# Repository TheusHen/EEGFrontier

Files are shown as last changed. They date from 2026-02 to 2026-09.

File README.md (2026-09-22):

# EEGFrontier V1



> [!WARNING]
> **Hardware V2 Under Development**
> The current version of this project (V1) has pending schematic and layout revisions. **V2 is under active development** with all necessary fixes. If you plan to fabricate or assemble this board, please **wait for the official V2 tag and release** before sending files to the fab.

EEGFrontier V1 is a compact EEG acquisition board built around the **ADS1299-4PAGR** and a **Seeed XIAO RP2040**.

This repository contains:
- Hardware design files (KiCad)
- Firmware (PlatformIO / Arduino)
- Project assets and documentation images

## Important Notice

Please check the `bom/` folder for the Bill of Materials and pricing information. A dedicated folder was created specifically to document BOM details and cost references.

## Short Project Description

**EEGFrontier V1** is an open-source EEG acquisition board designed to capture real brain signals and stream them in real time to a computer for analysis and visualization.
It focuses on learning, experimentation, and understanding attention and focus using raw EEG data.

---

## How to Use the Project

The board connects to EEG electrodes and streams data over USB to a computer.
Users flash the firmware to the XIAO RP2040, connect electrodes to the header, and read real-time EEG data using serial tools or custom software written in any language.

## Why I Made This Project

I made EEGFrontier to learn how real EEG hardware works beyond black-box consumer devices.
The goal is to make neurotechnology more accessible to students by providing a platform where raw signals, hardware design, and firmware are fully open and modifiable.

---

## Project Concept

The board is designed to connect dry electrodes and stream real-time data from the EEG channels.

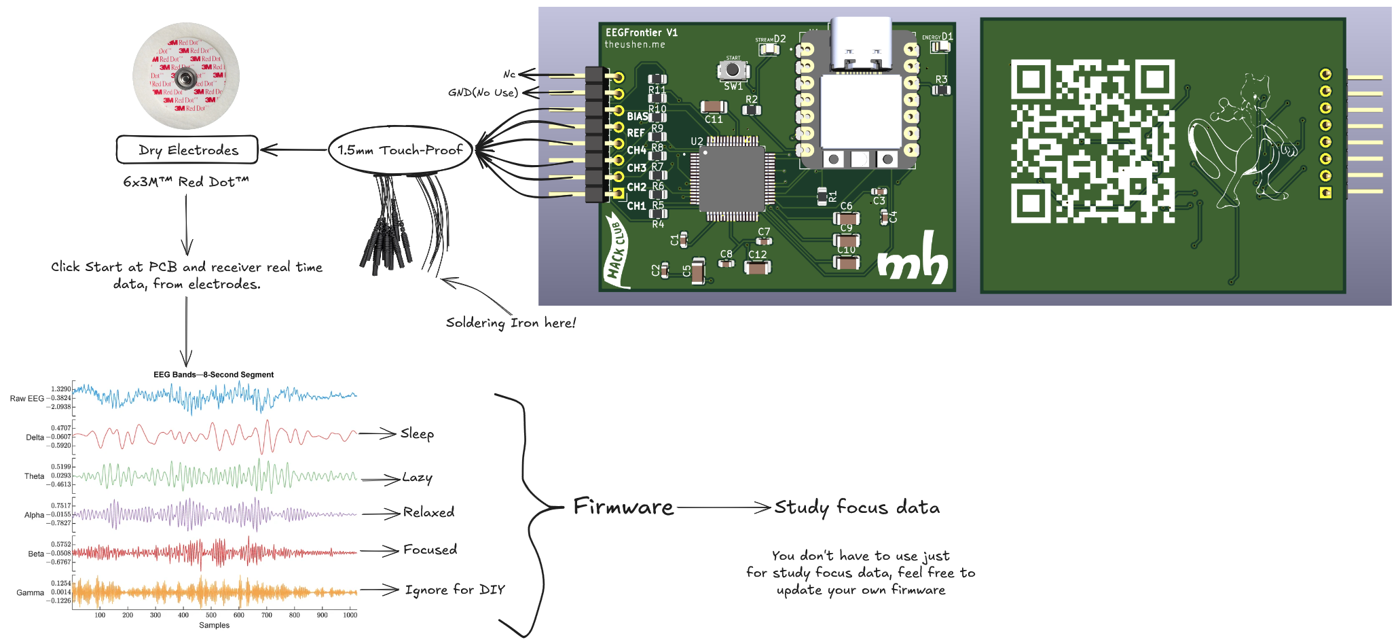
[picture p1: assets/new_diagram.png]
EEGFrontier concept and wiring overview V2


## Hardware Overview

### 3D View (Front)

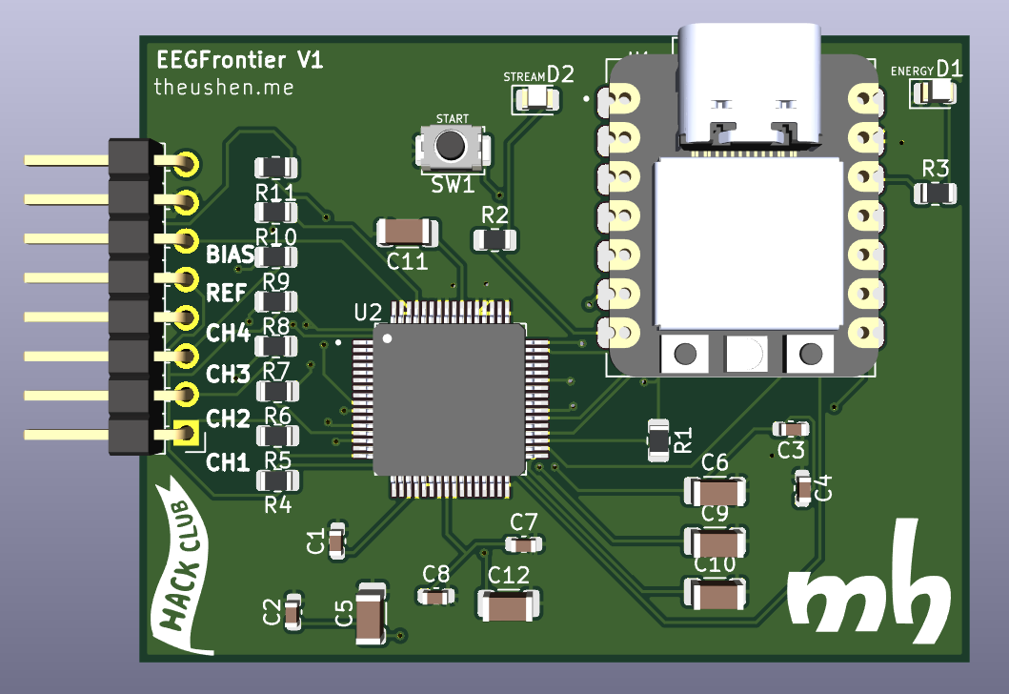
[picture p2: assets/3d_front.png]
EEGFrontier V1 3D front view


### 3D View (Back)

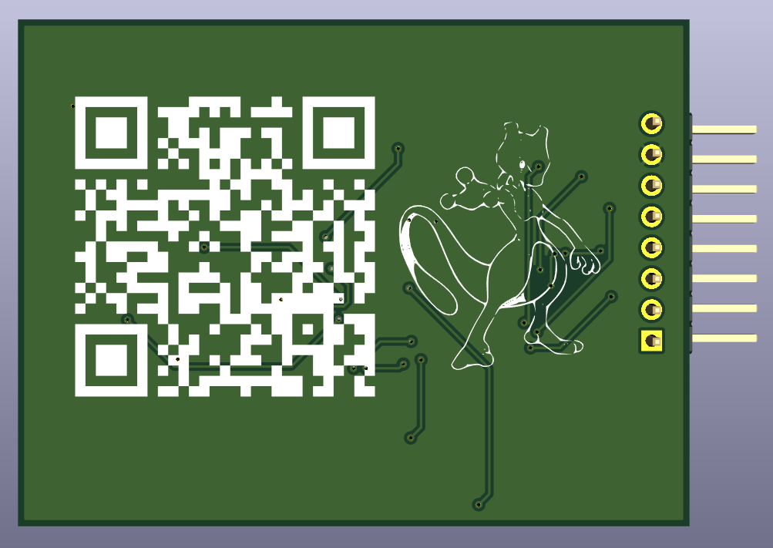
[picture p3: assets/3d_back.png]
EEGFrontier V1 3D back view


### PCB Layout

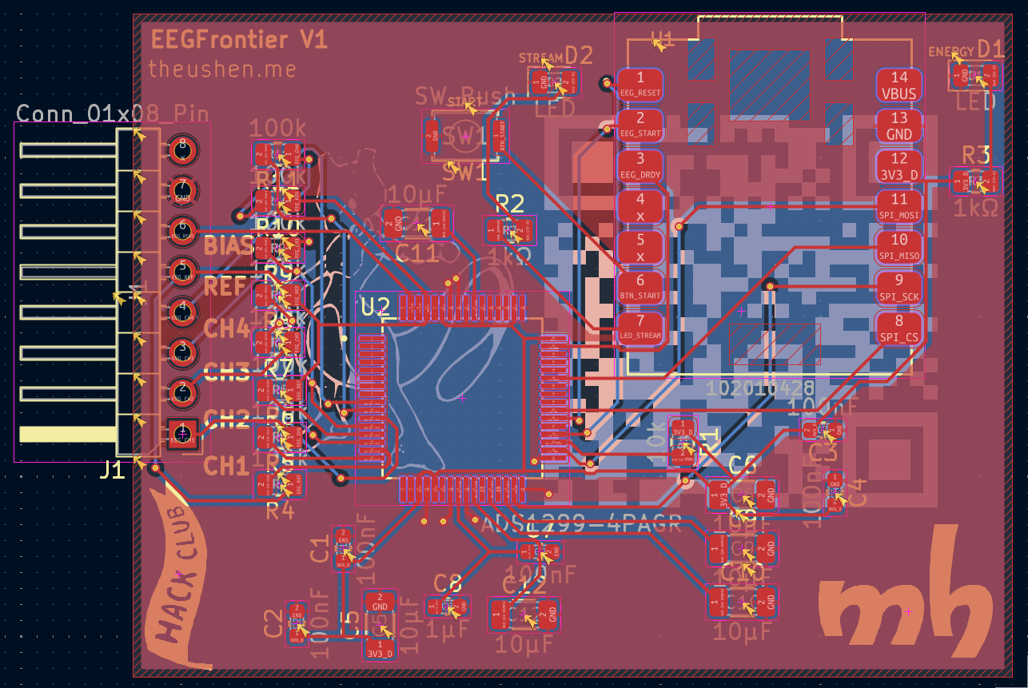
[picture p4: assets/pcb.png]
EEGFrontier V1 PCB layout


### Schematic

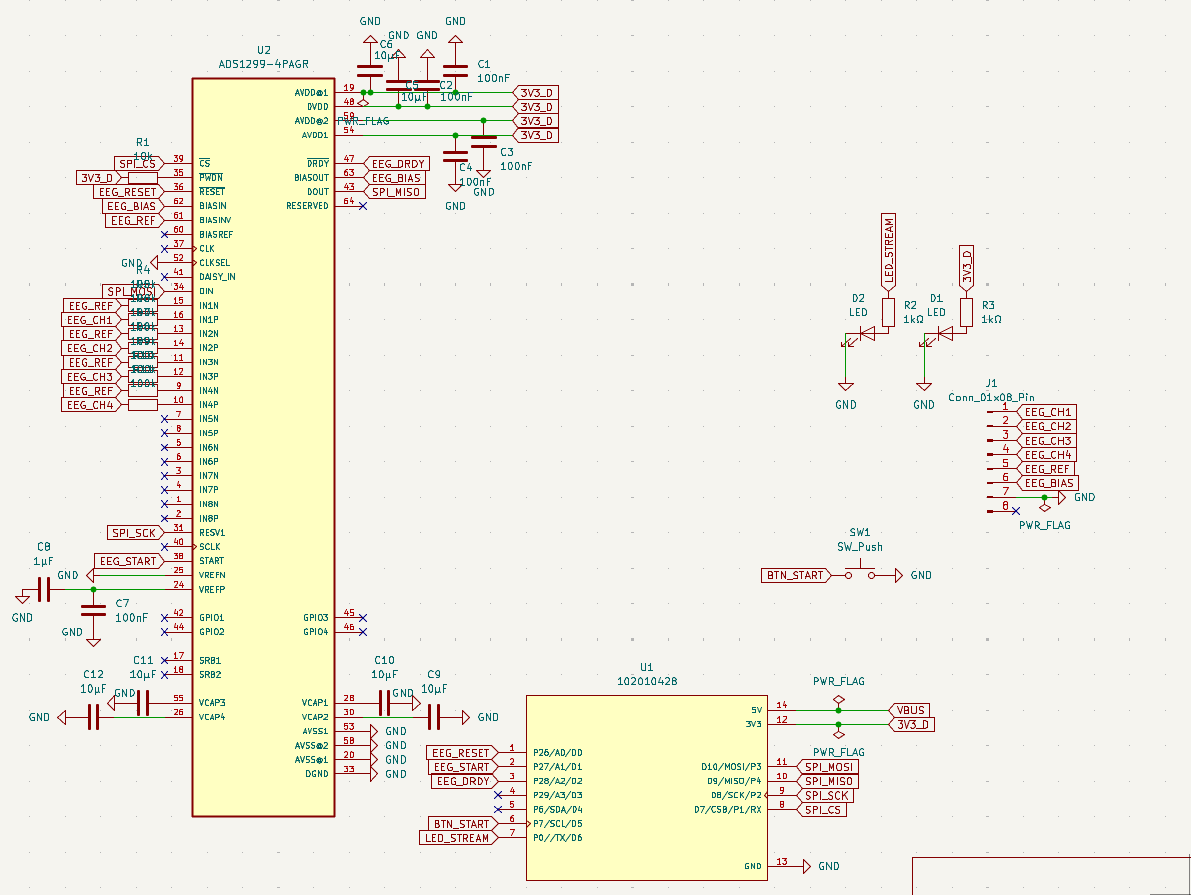
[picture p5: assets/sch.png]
EEGFrontier V1 schematic


## Quick Start

1. Flash the firmware to the Seeed XIAO RP2040 using PlatformIO
2. Connect the EEGFrontier board via USB
3. Attach EEG electrodes (channels, REF, BIAS)
4. Open Pendulum or a serial monitor
5. Start streaming with the `START` command

## Hardware Highlights

- ADS1299-based 4-channel EEG analog front-end
- Seeed XIAO RP2040 as main controller
- Header for EEG channels plus reference and bias
- Start button input (`BTN_START`)
- Status LEDs (power and stream/activity)
- Compact PCB with front/back annotated design

## Firmware Overview

The firmware (in `firmware/`) provides:
- ADS1299 initialization and register configuration
- DRDY interrupt-based sampling
- Binary streaming protocol (COBS + CRC16)
- CSV debug mode
- Serial commands for diagnostics and control
- Recovery logic for acquisition timeout
- Self-test and lead-off diagnostics

## Firmware Build (PlatformIO)

```bash
cd firmware
pio run -e xiao_rp2040
```

Monitor (default baud rate is `921600`):

```bash
cd firmware
pio device monitor -b 921600
```

## Serial Commands (Firmware)

- `HELP`
- `INFO`
- `STATS`
- `REGS`
- `START`
- `STOP`
- `MODE BIN`
- `MODE CSV`
- `REINIT`
- `TEST ON`
- `TEST OFF`
- `SELFTEST`
- `LOFF ON`
- `LOFF OFF`
- `LOFF STATUS`
- `PING`

## Technical Specifications

- Channels: 4 EEG channels + REF + BIAS
- ADC: 24-bit (ADS1299)
- Sampling rate: configurable (up to ADS1299 limits)
- Interface: USB (CDC)
- Power: USB 5V

## Repository Structure

- `firmware/` - PlatformIO firmware for XIAO RP2040 + ADS1299
- `assets/` - Images used in this README
- `EEGFrontier.kicad_sch` / `EEGFrontier.kicad_pcb` - KiCad project files
- `Pendulum` - Host software

## Pendulum

**Pendulum** is the host software suite for EEGFrontier: it reads EEG data over USB, offers a local web dashboard (Reflex), and includes a desktop monitor for real-time focus visualization.

For full setup and usage instructions, see `Pendulum/README.md`.

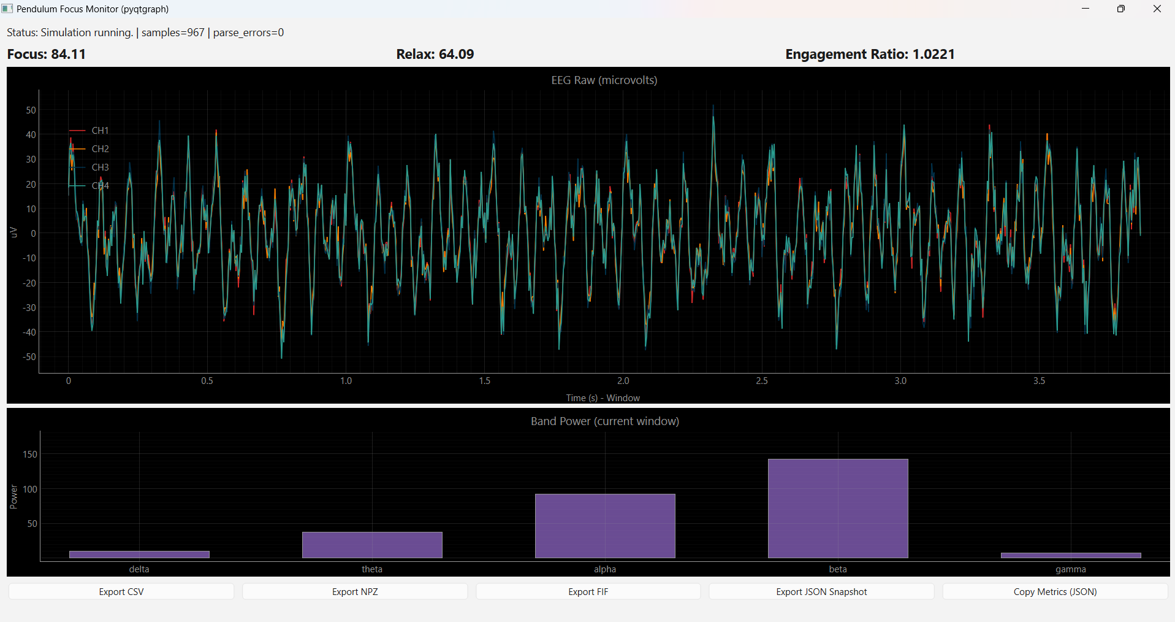
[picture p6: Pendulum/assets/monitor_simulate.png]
Pendulum desktop monitor


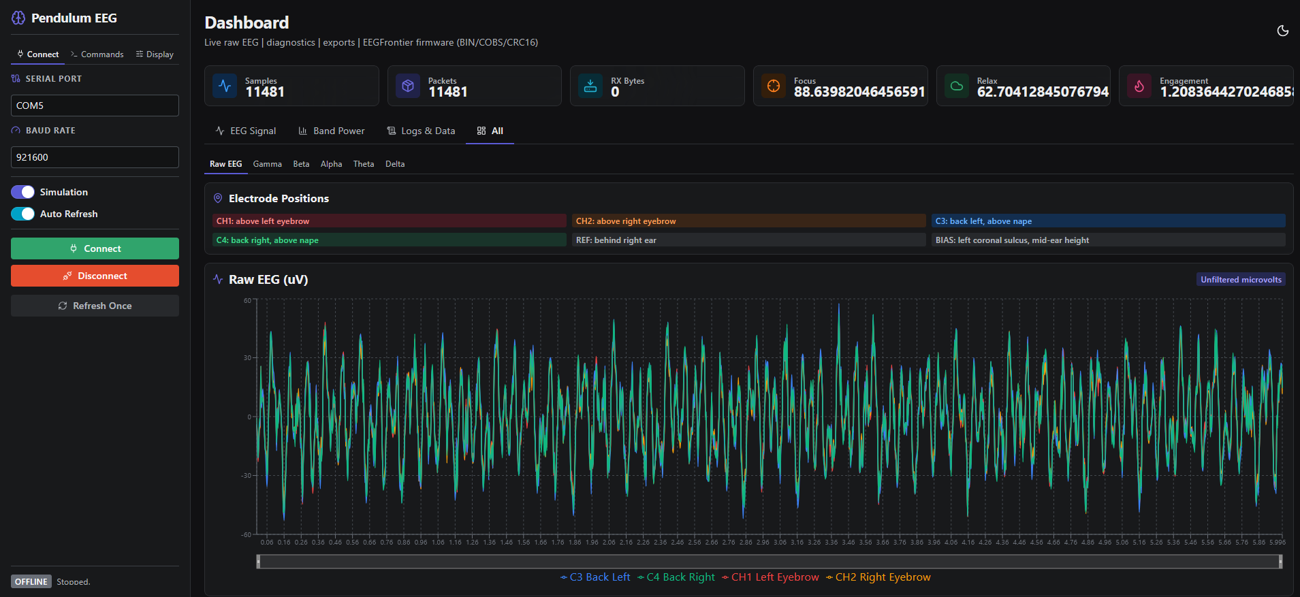
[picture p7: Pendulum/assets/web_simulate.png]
Pendulum web monitor


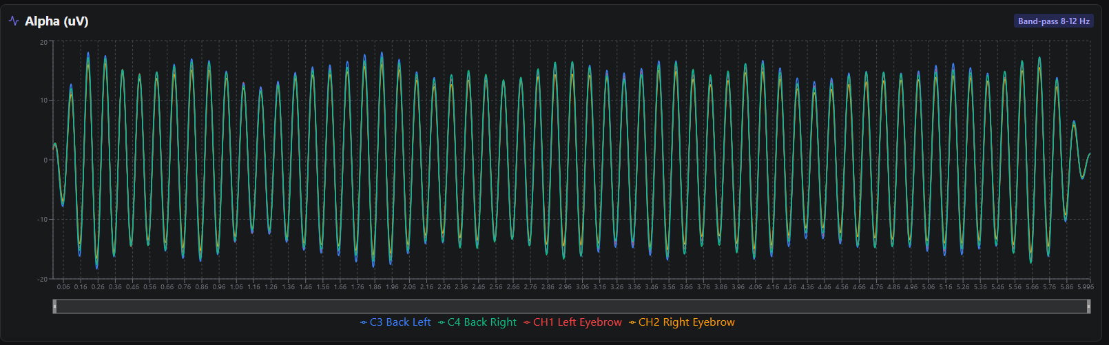
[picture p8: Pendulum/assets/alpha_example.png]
Pendulum result example


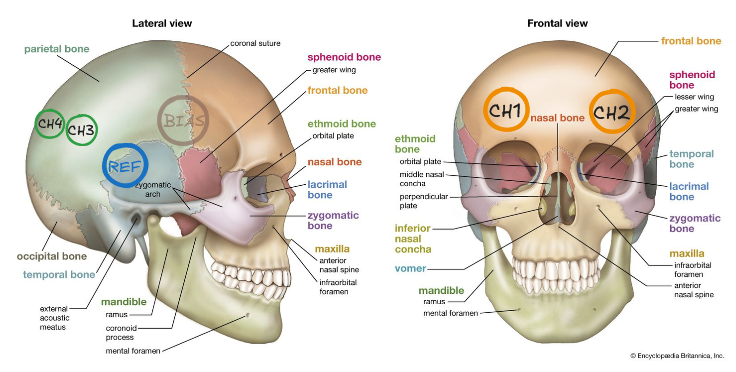
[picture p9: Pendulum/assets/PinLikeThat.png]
Pendulum interface detail


## If you are considering building this

I strongly recommend **not** attempting to fully hand-solder this PCB.

The board uses fine-pitch components and sensitive analog circuitry, which makes manual soldering difficult and error-prone. Instead, consider ordering the PCB **fully assembled** from a service such as **JLCPCB**.

If needed, you can then hand-solder only a few missing components — or none at all if everything is available for assembly.

## Safety & Protection

⚠️ **Important Safety Notice**

This device interfaces electrically with the human body and must be used with caution.

- This project **does not include medical-grade isolation** and **must never be connected to mains-powered equipment** without proper USB isolation.
- Always operate the device using a **battery-powered computer** or a **USB isolator** specifically designed for biomedical signals.
- Never use the device if any part of the circuit is damaged, exposed, or improperly assembled.
- Ensure electrodes and cables are clean, dry, and in good condition before use.
- Do **not** use this device on individuals with implanted electronic devices (e.g. pacemakers).
- This project is intended **strictly for research, education, and experimentation**.

The author assumes **no responsibility for misuse**, improper assembly, or unsafe operating conditions.

By using or building this device, you acknowledge that you understand the risks involved in working with bioelectrical signals and accept full responsibility for its use.

## Medical Disclaimer

This project is **not a medical device** and is **not intended for diagnosis, treatment, or clinical use**.

Any data produced by this device should be considered experimental and for educational or research purposes only.

## Known Limitations

- No medical-grade isolation
- No onboard battery
- Susceptible to motion artifacts with dry electrodes
- Requires external software for filtering and analysis(e.g. Pendulum)

## License

This project is released under the MIT License.
See the `LICENSE` file for details.

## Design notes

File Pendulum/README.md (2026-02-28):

# Pendulum EEG Suite

## This directory/software won't be nessesary a review from HackClub Reviewer
> Note for reviwer.

This directory includes software for EEG reading from USB port, not an firmware part.

Pendulum is the host software for EEGFrontier hardware. It follows the firmware
protocol from `firmware/` and provides:

- A local Reflex web dashboard (raw data, diagnostics, export tools).
- A desktop pyqtgraph app focused on real-time focus analysis.
- A simulation mode for development without hardware connected.

## Stack

- Python 3.11+
- Reflex
- pyserial
- numpy
- scipy
- pyqtgraph + PyQt6
- mne

## Setup

```bash
cd Pendulum
python -m venv .venv
.venv\Scripts\activate
pip install -U pip
pip install -e .
```

## Run

### 1) Web dashboard (Reflex)

```bash
cd Pendulum
reflex run
```

Open the localhost URL shown by Reflex.

If you hit frontend bootstrap issues on Windows (bun/npm path), use:

```powershell
.\run_reflex.ps1
```

or:

```bat
run_reflex.bat
```

If you need to stop all running Reflex instances:

```powershell
.\stop_reflex.ps1
```

### 2) Desktop focus monitor (pyqtgraph)

With hardware:

```bash
python -m pendulum_eeg.pyqt_focus --port COM5
```

Simulation:

```bash
python -m pendulum_eeg.pyqt_focus --simulate
```

## Firmware Protocol (BIN mode)

Packet format:

- `packet = COBS(raw_packet) + 0x00`
- `raw_packet = [type][ver][payload...][crc16_le]`

Packet types:

- `0x01`: sample
- `0x02`: event
- `0x7F`: error

Sample payload:

- `sample_index` `u32`
- `t_us` `u32`
- `status24` `u32`
- `ch1..ch4` `i32`
- `flags` `u32`
- `missed_drdy_frame` `u32`
- `recoveries_total` `u32`

## Export formats

- `exports/*.csv`
- `exports/*.npz`
- `exports/*.json`
- `exports/*.fif` (MNE)

## Notes

- Default serial baud: `921600`
- Default firmware sample rate: `250 SPS`
- Focus score is a real-time heuristic from EEG bands and should be calibrated
  per user/protocol for serious studies.

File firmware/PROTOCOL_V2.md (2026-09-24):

# EEGFrontier Firmware V2 Protocol (V2 isolated board)

Framing is unchanged from V1 so existing Pendulum builds keep working.
V2 only adds event/error codes and documents the current defaults.

## Framing

```
packet = COBS(raw_packet) + 0x00
raw_packet = [type:u8][ver:u8][payload...][crc16_le:u16]
crc = CRC16-CCITT (poly 0x1021, init 0xFFFF) over everything before crc
```

Max raw sizes: sample 44 B, event 17 B, error 13 B. Encoded form never
contains `0x00` except the delimiter.

## Packet types

| type | name | payload | notes |
|------|------|---------|-------|
| 0x01 | SAMPLE | `sample_index:u32 t_us:u32 status24:u32 ch1..ch4:i32 flags:u32 missed_drdy_frame:u32 recoveries_total:u32` | Layout frozen. `sample_index` is monotonic since boot, never reset by START/STOP/recovery. |
| 0x02 | EVENT | `event_code:u8 a:u32 b:u32 c:u32` | Additive codes below. Old hosts log unknown codes as `EVENT`. |
| 0x7F | ERROR | `error_code:u8 a:u32 b:u32` | Additive codes below. |

`ver` is currently `0x01` for all three.

## Flags (sample.flags)

Bits 0-6 are frozen:

- 0 STREAMING, 1 RECOVERED, 2 BTN_TOGGLED, 3 DRDY_MISSED,
  4 STATUS_INVALID, 5 ADS_LOFF_ANY, 6 TX_OVERFLOW

V2 adds bit 7 CONFIG_CHANGED (SPS/GAIN/VREF changed since last frame).

## Events

| code | name | a | b | c |
|------|------|---|---|---|
| 0x01 | STREAM_STATE | 1=on 0=off | session_id or sample_index | sps |
| 0x02 | HELLO | fw + proto | sps | gain + vref |
| 0x10 | ADS_INIT_OK | ads_id | attempt | sps |
| 0x11 | PONG | seq | micros | 0 |
| 0x30 | SELFTEST | 1=pass 0=fail | good_frames | status_bad |
| 0x31 | CONFIG | sps | gain | vref_mv (or min_p2p in selftest follow-up) |
| 0x32 | TX_HIGH_WATER | queued | dropped_packets | 0 |

HELLO packing: `a = (2<<24)|(1<<16)|PROTO_VER`,
`b = sps`, `c = (gain<<24)|(vref_mv & 0xFFFFFF)`.

On boot the device emits `# BOOT` text, `HELLO`, then `ADS_INIT_OK` (or
`ADS_INIT_FAIL`). After a watchdog reboot it first emits an additional
`HELLO` event with `a = 'RBOT'`.

## Errors

| code | name | meaning |
|------|------|---------|
| 0xE1 | ADS_INIT_FAIL | ADC not responding after retries |
| 0xE2 | FRAME_READ_FAIL | SPI read failed |
| 0xE3 | DRDY_TIMEOUT | no frame for 8x period, re-sync follows |
| 0xE4 | TX_OVERFLOW | (reserved, overflow is flagged in-sample) |
| 0xE5 | BUSY | register command refused while streaming |

`REGS` and `INFO` ID reads refuse while streaming (`BUSY`) instead of
corrupting RDATAC. `STATS` never touches SPI and is always safe.

## Serial commands

```
HELP  INFO  STATS  REGS  START  STOP  MODE BIN  MODE CSV
REINIT  TEST ON|OFF  SELFTEST  LOFF ON|OFF|STATUS
SPS 250|500|1000  GAIN 1|2|4|6|8|12|24  VREF 4500
PING [seq]
```

`MODE CSV` is debug only and throttled: when the TX queue passes the
high-water mark, frames are dropped and counted rather than stalling
acquisition.

## Defaults on the V2 board

- SPS 250, GAIN 24, internal VREF 4500.
- The ADS1299-4 internal reference is fixed at 4.5 V. `VREF 2400` is
  rejected; the host must use `ads_vref_uv=4500000` (HELLO/INFO) for
  conversion: `uV = counts * vref_uv / (gain * 8388607)`.
- AVDD/AVSS are 5V_A/GND_A from the isolated supply; DVDD is 3V3_D_ISO.
- SPI/control and both supply rails cross the USB-to-EEG isolation barrier.
  This research board is not IEC 60601-1 certified.
- SPI 2 MHz, TX ring 16 KB, watchdog 2 s.
- Button: short press toggles stream, 1.5 s hold runs SELFTEST.

## Register map audit (ADS1299, internal 2.048 MHz clock)

- CONFIG1: 0x96=250, 0x95=500, 0x94=1000 (HR mode).
- CONFIG2: 0xD0 normal, 0xD3 test-signal.
- CONFIG3: 0xEC enables the internal reference buffer, internal BIASREF,
  and BIAS amplifier; reserved bits [6:5] are written as required by TI.
- LOFF 0x13 with SENSP/SENSN 0x0F when diagnostics on, else 0x00.
- CHnSET: gain bits in [6:4] (24x=0x60), MUX normal 0x00 / test 0x05.
- BIAS_SENSP/SENSN 0x0F, GPIO 0x0C, MISC1/2 0x00, CONFIG4 0x00.
- ID reset value 0x1E (0x12 seen on some lots); anything else logs a
  warning event but does not block init unless 0x00/0xFF.
- Allow 150 ms for the internal reference to settle after CONFIG3 enables it.
- The fitted ADS1299-4 has four measurement channels; firmware configures
  and validates CH1SET–CH4SET and lead-off diagnostics only for those channels.

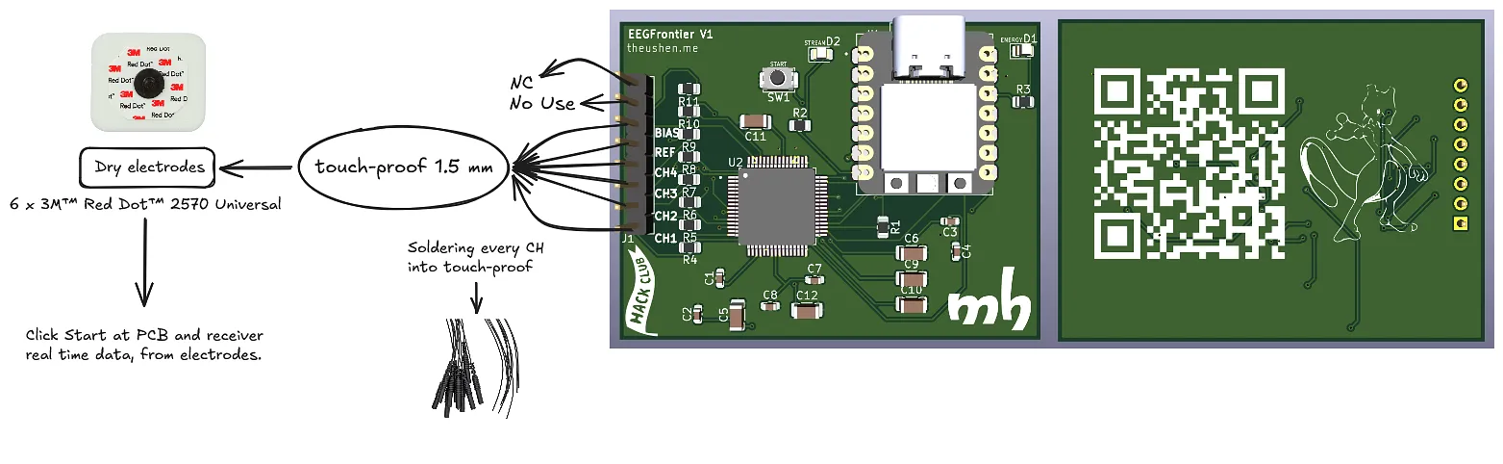
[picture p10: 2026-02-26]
assets/diagram.png

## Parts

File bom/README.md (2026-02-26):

# BOM and Price Notes (EEGFrontier V1)

This folder contains the Bill of Materials references, price snapshots, and purchase/cart screenshots used for the **EEGFrontier V1** prototype.

## Important Notes

- Prices are a snapshot and may change over time.
- Shipping/import costs can vary by country and carrier.
- The USD values below follow the original CSV notation and include mixed formatting from the vendor/cart screenshots.

## Files in This Folder

- `ibom.html` - Interactive BOM export
- `pcb_bom.png` - BOM placement/table screenshot
- `assets/` - Vendor/product/cart screenshots

## Price Table (replicated from `Prices.csv`)

| URL / Vendor | Item | Qty | Product + Shipping | USD (5.14 BRL/USD) |
| --- | --- | --- | --- | --- |
| https://www.santoantoniodist.com.br/eletrodo3m/prod-9760997/ | Eletrodo 3M | 1x50 | R$ 37,90 + R$ 24,20 | USD $12,08 |
| https://shop.neurospec.com/1-5mm-touchproof-female-to-open-lead-cable-5-pack | 1.5mm Touch-Proof (TP) Female to Open Lead Cable (5/pack) | 2x5 | R$ 413,81 + R$ 283,75 | USD $135,70 |
| br.mouser.com | ADS1299-4PAGR | 1x1 | Included in Mouser cart | Mouser Cart: $79.85 |
| www.digikey.com.br | Push Button | 1x1 | Included in DigiKey cart | DigiKey Cart: $46,83 |
| br.mouser.com | Header 1x08 | 1x1 | Included in Mouser cart | Mouser Cart: $79.85 |
| br.mouser.com | LEDs 0805 | 1x2 | Included in Mouser cart | Mouser Cart: $79.85 |
| www.digikey.com.br | 0805 Resistors | 1x11 | Included in DigiKey cart | DigiKey Cart: $46,83 |
| www.digikey.com.br | 1µF 0603 capacitor | 1x1 | Included in DigiKey cart | DigiKey Cart: $46,83 |
| www.digikey.com.br | 100nF 0603 capacitor | 1x5 | Included in DigiKey cart | DigiKey Cart: $46,83 |
| www.digikey.com.br | 10µF 1206 capacitor | 1x6 | Included in DigiKey cart | DigiKey Cart: $46,83 |

### Estimated Total

- **Total: $274,46** (as recorded in the original price sheet)

## BOM / Placement Reference

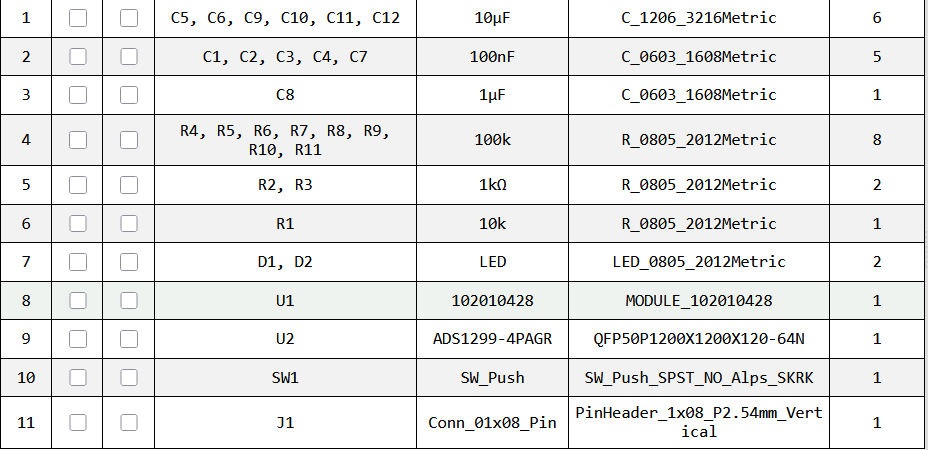
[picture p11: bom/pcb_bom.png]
PCB BOM table screenshot


## Component / Purchase References

### Electrodes (3M Red Dot)

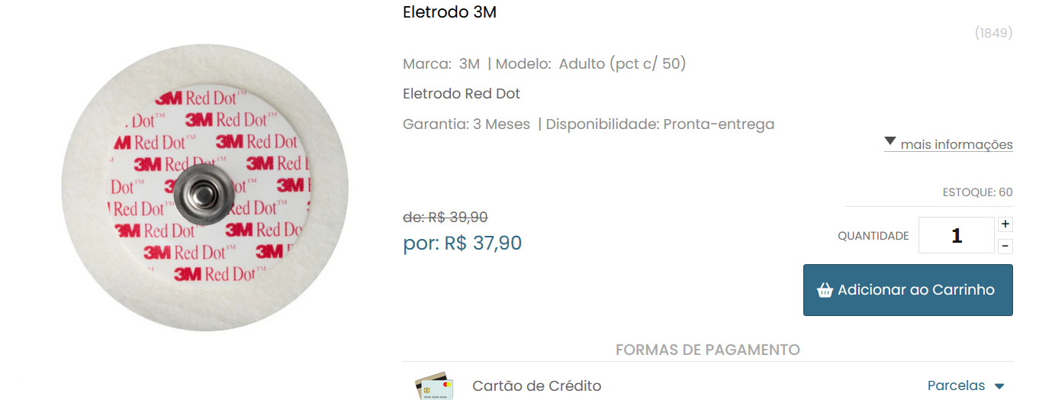
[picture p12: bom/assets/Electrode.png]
Electrode 3M product screenshot


### Touch-Proof Cables

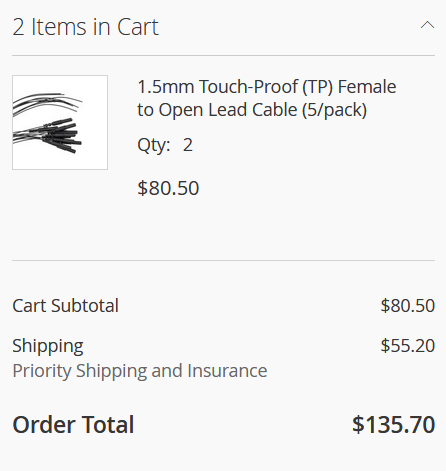
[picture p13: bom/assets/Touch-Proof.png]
Touch-proof cable cart screenshot


### DigiKey Items (components list)

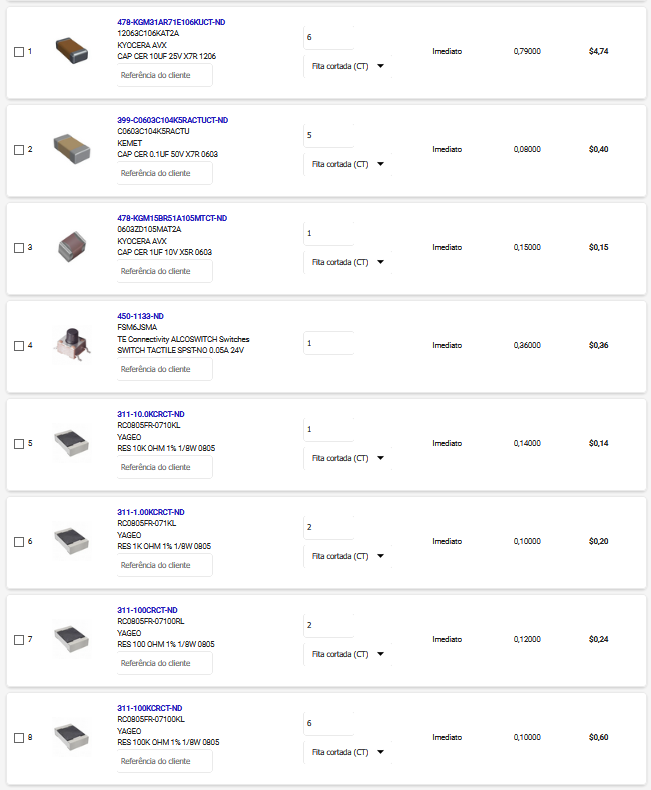
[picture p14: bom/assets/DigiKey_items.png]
DigiKey items screenshot


### DigiKey Cart Summary

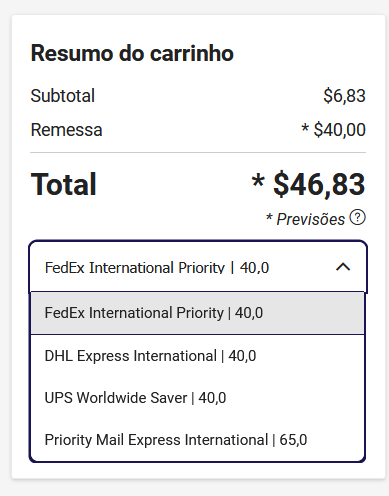
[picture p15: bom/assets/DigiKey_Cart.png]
DigiKey cart summary screenshot


### Mouser Cart Summary

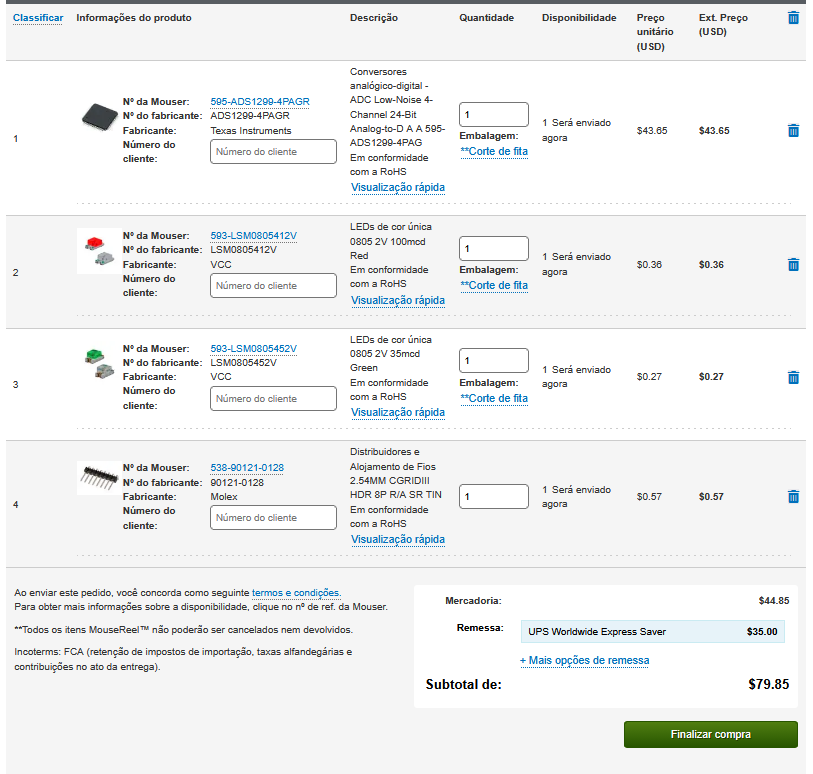
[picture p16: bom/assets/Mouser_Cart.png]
Mouser cart summary screenshot


## Notes for Rebuilds

- Re-quote Mouser and DigiKey carts before ordering.
- Confirm local availability/substitutions for passives and LEDs.
- Review `ibom.html` together with the KiCad PCB file before assembling.

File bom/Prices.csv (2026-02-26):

Url | Name | Qnt. | (Product + Ship) | USD(5,14 R$)
https://www.santoantoniodist.com.br/eletrodo3m/prod-9760997/ | Eletrodo 3M | 1x50 | R$ 37,90 + R$ 24,20 | USD $12,08
https://shop.neurospec.com/1-5mm-touchproof-female-to-open-lead-cable-5-pack | 1.5mm Touch-Proof (TP) Female to Open Lead Cable (5/pack) | 2x5 | R$ 413,81 + R$ 283,75 | USD $135,70
br.mouser.com | ADS1299-4PAGR | 1x1 |  | Mouser Cart: $79.85
www.digikey.com.br | Push Button | 1x1 |  | DigiKey Cart: $46,83
br.mouser.com | Header 1x08 | 1x1 |  | Mouser Cart: $79.85
br.mouser.com | LEDs 0805 | 1x2 |  | Mouser Cart: $79.85
www.digikey.com.br | 0805 Resistors | 1x11 |  | DigiKey Cart: $46,83
www.digikey.com.br | 1µF 0603 capacitor | 1x1 |  | DigiKey Cart: $46,83
www.digikey.com.br | 100nF 0603 capacitor | 1x5 |  | DigiKey Cart: $46,83
www.digikey.com.br | 10µF 1206 capacitor | 1x6 |  | DigiKey Cart: $46,83
Total: $274,46

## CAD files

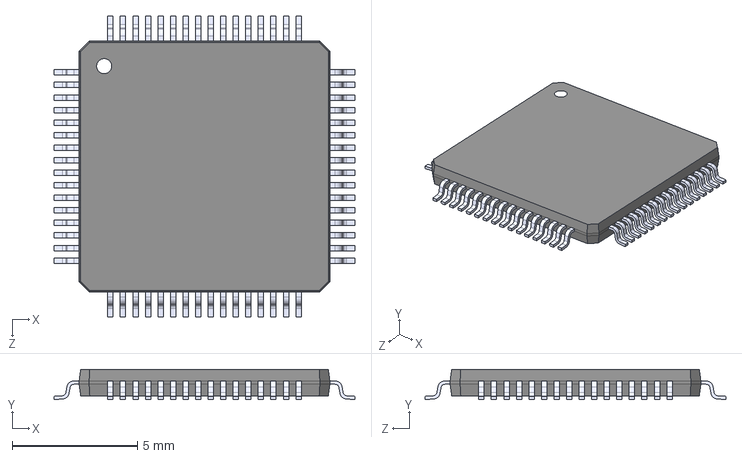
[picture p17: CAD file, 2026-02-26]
ADS1299-4PAGR/ADS1299-4PAGR.step
12.0 x 1.20 x 12.0 mm

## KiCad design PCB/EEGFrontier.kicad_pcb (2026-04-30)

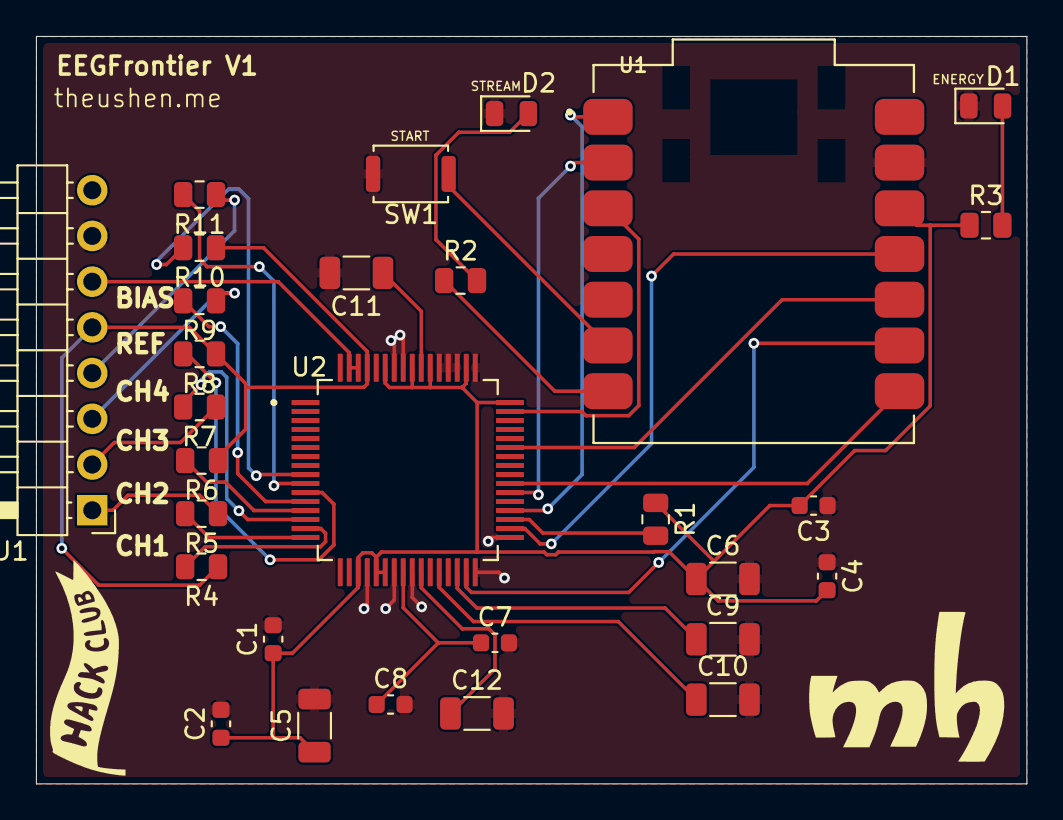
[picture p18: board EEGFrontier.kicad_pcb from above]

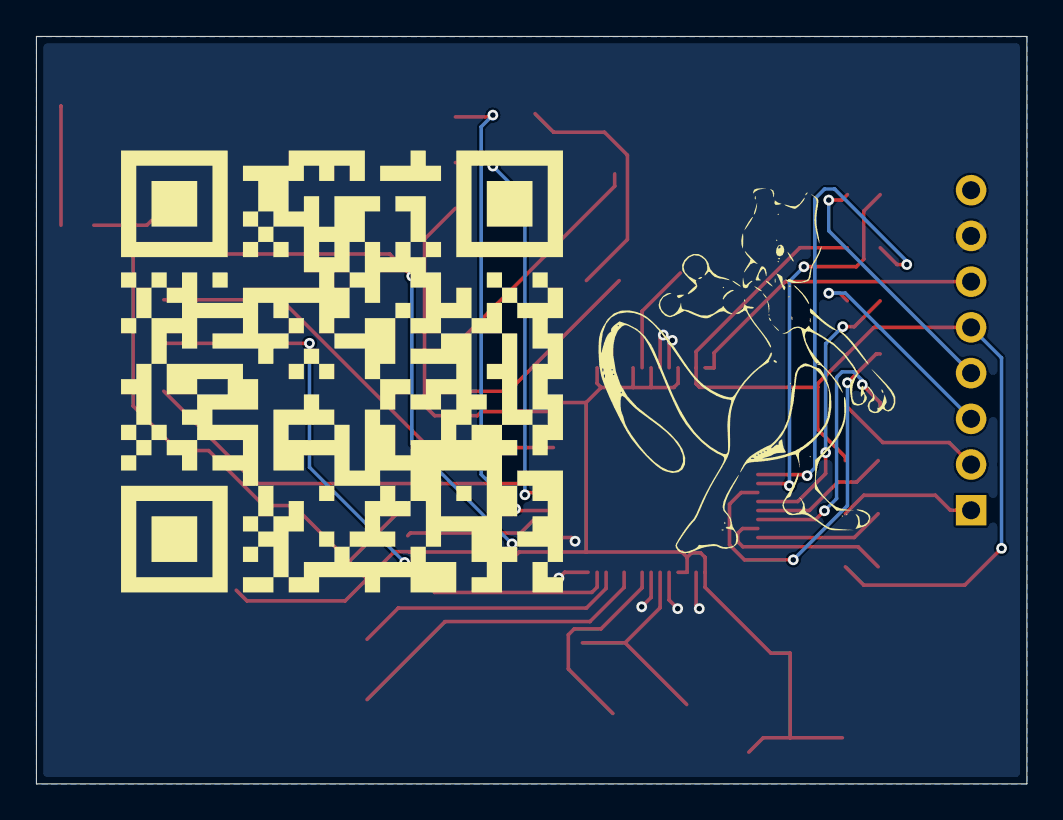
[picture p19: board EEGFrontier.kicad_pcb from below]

Board: 2 copper layers, 55.0 x 41.5 mm, 33 parts (2 on the bottom side), 33 nets.

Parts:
C1, C2, C3, C4, C7: 100nF; C_0603_1608Metric
C5, C6, C9, C10, C11, C12: 10µF; C_1206_3216Metric
C8: 1µF; C_0603_1608Metric
D1, D2: LED; LED_0805_2012Metric
G1, G2, G4, G5: LOGO
J1: Conn_01x08_Pin; PinHeader_1x08_P2.54mm_Horizontal
R1: 10k; R_0805_2012Metric
R2, R3: 1kΩ; R_0805_2012Metric
R4, R5, R6, R7, R8, R9, R10, R11: 100k; R_0805_2012Metric
SW1: SW_Push; SW_Push_SPST_NO_Alps_SKRK
U1: 102010428; MODULE_102010428
U2: ADS1299-4PAGR; QFP50P1200X1200X120-64N

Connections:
3V3_D: C1.1, C2.1, C3.2, C4.2, C5.1, C6.1, R1.1, R3.1, U1.12 (3V3), U2.19 (AVDD@1), U2.21 (AVDD@1), U2.22 (AVDD@1), U2.48 (DVDD), U2.50 (DVDD), U2.54 (AVDD1), U2.56 (AVDD@1), U2.59 (AVDD@2)
BTN_START: SW1.1, U1.6 (P7/SCL/D5)
EEG_BIAS: J1.6, U2.62 (BIASIN), U2.63 (BIASOUT)
EEG_CH1: J1.1, R5.1
EEG_CH2: J1.2, R7.1
EEG_CH3: J1.3, R9.1
EEG_CH4: J1.4, R11.1
EEG_DRDY: U1.3 (P28/A2/D2), U2.47 (~DRDY)
EEG_REF: J1.5, R4.1, R6.1, R8.1, R10.1, U2.61 (BIASINV)
EEG_RESET: U1.1 (P26/A0/D0), U2.36 (~RESET)
EEG_START: U1.2 (P27/A1/D1), U2.38 (START)
GND: C1.2, C2.2, C3.1, C4.1, C5.2, C6.2, C7.2, C8.2, C9.2, C10.2, C11.2, C12.2, D1.1 (K), D2.1 (K), J1.7, SW1.2, U1.13 (GND), U2.20 (AVSS@1), U2.23 (AVSS@1), U2.25 (VREFN), U2.32 (AVSS@1), U2.33 (DGND), U2.49 (DGND), U2.51 (DGND), U2.52 (CLKSEL), U2.53 (AVSS1), U2.57 (AVSS@1), U2.58 (AVSS@2)
LED_STREAM: R2.1, U1.7 (P0//TX/D6)
unnamed: D1.2 (A), R3.2
unnamed: D2.2 (A), R2.2
unnamed: R4.2, U2.15 (IN1N)
unnamed: R5.2, U2.16 (IN1P)
unnamed: R6.2, U2.13 (IN2N)
unnamed: R7.2, U2.14 (IN2P)
unnamed: R8.2, U2.11 (IN3N)
unnamed: R9.2, U2.12 (IN3P)
unnamed: R10.2, U2.9 (IN4N)
unnamed: R11.2, U2.10 (IN4P)
unnamed: C10.1, U2.28 (VCAP1)
unnamed: C9.1, U2.30 (VCAP2)
unnamed: C11.1, U2.55 (VCAP3)
unnamed: C12.1, U2.26 (VCAP4)
unnamed: C7.1, C8.1, U2.24 (VREFP)
unnamed: R1.2, U2.35 (~PWDN)
SPI_CS: U1.8 (D7/CSB/P1/RX), U2.39 (~CS)
SPI_MISO: U1.10 (D9/MISO/P4), U2.43 (DOUT)
SPI_MOSI: U1.11 (D10/MOSI/P3), U2.34 (DIN)
SPI_SCK: U1.9 (D8/SCK/P2), U2.31 (RESV1)

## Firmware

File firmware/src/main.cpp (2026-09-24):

#include <Arduino.h>
#include <SPI.h>

#include "ads1299_driver.h"
#include "fw_commands.h"
#include "fw_config.h"
#include "fw_protocol.h"
#include "fw_state.h"
#include "fw_tx.h"
#include "fw_watchdog.h"

namespace {

void blinkCode(uint8_t times, uint16_t onMs = 120) {
  for (uint8_t i = 0; i < times; i++) {
    digitalWrite(PIN_LED_STREAM, HIGH);
    delay(onMs);
    digitalWrite(PIN_LED_STREAM, LOW);
    delay(onMs);
  }
}

}  // namespace

void setup() {
  pinMode(PIN_EEG_RESET, OUTPUT);
  pinMode(PIN_EEG_START, OUTPUT);
  pinMode(PIN_SPI_CS, OUTPUT);
  pinMode(PIN_LED_STREAM, OUTPUT);

  pinMode(PIN_EEG_DRDY, INPUT_PULLUP);
  pinMode(PIN_BTN_START, INPUT_PULLUP);

  digitalWrite(PIN_SPI_CS, HIGH);
  digitalWrite(PIN_EEG_RESET, HIGH);
  digitalWrite(PIN_EEG_START, LOW);
  digitalWrite(PIN_LED_STREAM, LOW);

  Serial.begin(SERIAL_BAUD);
  txInit();

  // Give USB CDC a moment to enumerate without stalling forever on
  // battery-powered setups where nobody opens the port.
  uint32_t bootStart = millis();
  while (!Serial && static_cast<uint32_t>(millis() - bootStart) < 400) {
    delay(5);
  }

  SPI.setSCK(PIN_SPI_SCK);
  SPI.setTX(PIN_SPI_MOSI);
  SPI.setRX(PIN_SPI_MISO);
  SPI.begin();

  attachInterrupt(digitalPinToInterrupt(PIN_EEG_DRDY), onDrdyFalling, FALLING);

  fwWatchdogInit(2000);

  printLine("");
  printLine("# BOOT EEGFrontier_V2");
  printLine("# DEFAULT MODE BIN");
  printLine("# hardware_isolation=USB_to_EEG_SPI_and_power");
  printLine("# WARN research hardware; isolation is not IEC 60601-1 certified");
  printHelp();

  if (g_watchdogRebootDetected) {
    emitEventPacket(EVT_HELLO, 0x5242544CUL /*RBOT*/, g_recoveriesTotal, 0);
  }
  emitHelloPacket();
  bool ok = adsInitRobust();
  g_lastGoodFrameUs = micros();
  if (!ok) {
    blinkCode(2);
  }
  txService();
}

void loop() {
  fwWatchdogFeed();
  txService();
  handleSerialCommands();
  handleButton();

  if (g_streaming) {
    // Drain at most one frame per loop so commands stay responsive at
    // 500/1000 SPS. The DRDY flag coalesces overruns into missed counts.
    handleOneSampleFrame();
    txService();
  }

  recoverAdsIfNeeded();

  // Slow status blink while idle with lead-off or errors pending.
  static uint32_t lastIdleBlink = 0;
  if (!g_streaming) {
    uint32_t now = millis();
    if (static_cast<uint32_t>(now - lastIdleBlink) > 2000) {
      lastIdleBlink = now;
      if (!g_adsReady) {
        blinkCode(2, 80);
      }
    }
  }

  txService();
}

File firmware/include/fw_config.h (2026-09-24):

#pragma once

#include <Arduino.h>

// EEGFrontier V2 isolated board: XIAO RP2040 + ADS1299-4PAGR.
//
// PINOUT (unchanged from V1):
// D0  -> EEG_RESET
// D1  -> EEG_START
// D2  -> EEG_DRDY
// D5  -> BTN_START
// D6  -> LED_STREAM
// D7  -> SPI_CS
// D8  -> SPI_SCK
// D9  -> SPI_MISO
// D10 -> SPI_MOSI
//
// Serial commands (V2):
//   HELP
//   INFO
//   STATS
//   REGS
//   START
//   STOP
//   MODE BIN
//   MODE CSV        (debug only, throttled while streaming)
//   REINIT
//   PING [seq]
//   TEST ON | TEST OFF
//   SELFTEST
//   LOFF ON | LOFF OFF | LOFF STATUS
//   SPS 250 | 500 | 1000
//   GAIN 1 | 2 | 4 | 6 | 8 | 12 | 24
//   VREF 4500 (fixed internal ADS1299 reference)
//
// BIN protocol (unchanged framing, see firmware/PROTOCOL_V2.md):
//   packet = COBS(raw_packet) + 0x00
//   raw_packet = [type][ver][payload...][crc16_le]
//
// Types:
//   0x01 = sample packet (40 bytes raw, layout frozen for Pendulum compat)
//   0x02 = event/status packet
//   0x7F = error packet

// Firmware identity
constexpr char FW_NAME[] = "EEGFrontier";
constexpr char FW_VERSION[] = "2.1.0";
constexpr uint8_t FW_MAJOR = 2;
constexpr uint8_t FW_MINOR = 1;
constexpr uint16_t FW_VERSION_U16 = 0x0201;

// Pins
constexpr uint8_t PIN_EEG_RESET  = D0;
constexpr uint8_t PIN_EEG_START  = D1;
constexpr uint8_t PIN_EEG_DRDY   = D2;
constexpr uint8_t PIN_BTN_START  = D5;
constexpr uint8_t PIN_LED_STREAM = D6;

constexpr uint8_t PIN_SPI_CS     = D7;
constexpr uint8_t PIN_SPI_SCK    = D8;
constexpr uint8_t PIN_SPI_MISO   = D9;
constexpr uint8_t PIN_SPI_MOSI   = D10;

// Serial / SPI config
//
// NOTE: on the RP2040 native USB CDC the baud setting is ignored by the
// host driver; it only matters for real UART bridges. Kept so INFO stays
// honest about what the host asked for, and so serial monitors pick a
// fast default.
constexpr uint32_t SERIAL_BAUD  = 921600;
constexpr uint32_t SPI_CLOCK_HZ = 2000000;
#if !defined(CSV_DEBUG_ENABLED)
#define CSV_DEBUG_ENABLED 1  // CSV stays available but is throttled, debug only
#endif

// ADS1299-4PAGR uses the internal 4.5 V reference on this V2 board.
// AVDD is 5V_A (isolated); DVDD is 3V3_D_ISO. The ADS1299 internal
// reference is fixed at 4.5 V: it is not programmable to 2.4 V.
constexpr uint32_t ADS_VREF_UV_4500 = 4500000UL;
constexpr uint32_t ADS_VREF_UV = ADS_VREF_UV_4500;
constexpr uint8_t ADS_DEFAULT_GAIN = 24;
constexpr uint32_t ADS_DEFAULT_SPS = 250;
constexpr uint32_t ADS_DEFAULT_VREF_UV = ADS_VREF_UV_4500;
constexpr uint32_t ADS_DRDY_PERIOD_US = 1000000UL / ADS_DEFAULT_SPS;

// ADS1299 commands
constexpr uint8_t CMD_WAKEUP  = 0x02;
constexpr uint8_t CMD_STANDBY = 0x04;
constexpr uint8_t CMD_RESET   = 0x06;
constexpr uint8_t CMD_START   = 0x08;
constexpr uint8_t CMD_STOP    = 0x0A;
constexpr uint8_t CMD_RDATAC  = 0x10;
constexpr uint8_t CMD_SDATAC  = 0x11;
constexpr uint8_t CMD_RDATA   = 0x12;

// ADS1299 registers
constexpr uint8_t REG_ID          = 0x00;
constexpr uint8_t REG_CONFIG1     = 0x01;
constexpr uint8_t REG_CONFIG2     = 0x02;
constexpr uint8_t REG_CONFIG3     = 0x03;
constexpr uint8_t REG_LOFF        = 0x04;
constexpr uint8_t REG_CH1SET      = 0x05;
constexpr uint8_t REG_CH2SET      = 0x06;
constexpr uint8_t REG_CH3SET      = 0x07;
constexpr uint8_t REG_CH4SET      = 0x08;
constexpr uint8_t REG_BIAS_SENSP  = 0x0D;
constexpr uint8_t REG_BIAS_SENSN  = 0x0E;
constexpr uint8_t REG_LOFF_SENSP  = 0x0F;
constexpr uint8_t REG_LOFF_SENSN  = 0x10;
constexpr uint8_t REG_GPIO        = 0x14;
constexpr uint8_t REG_MISC1       = 0x15;
constexpr uint8_t REG_MISC2       = 0x16;
constexpr uint8_t REG_CONFIG4     = 0x17;

// Protocol constants (sample layout frozen; events/errors are additive)
constexpr uint8_t PKT_SAMPLE = 0x01;
constexpr uint8_t PKT_EVENT  = 0x02;
constexpr uint8_t PKT_ERROR  = 0x7F;
constexpr uint8_t PROTO_VER  = 0x01;

// Event codes (additive in V2, old hosts ignore unknown ones)
constexpr uint8_t EVT_STREAM_STATE = 0x01;
constexpr uint8_t EVT_HELLO        = 0x02;
constexpr uint8_t EVT_ADS_INIT_OK  = 0x10;
constexpr uint8_t EVT_PONG         = 0x11;
constexpr uint8_t EVT_SELFTEST     = 0x30;
constexpr uint8_t EVT_CONFIG       = 0x31;
constexpr uint8_t EVT_TX_HIGH_WATER = 0x32;

// Error codes (additive in V2)
constexpr uint8_t ERR_ADS_INIT_FAIL   = 0xE1;
constexpr uint8_t ERR_FRAME_READ_FAIL = 0xE2;
constexpr uint8_t ERR_DRDY_TIMEOUT    = 0xE3;
constexpr uint8_t ERR_TX_OVERFLOW     = 0xE4;
constexpr uint8_t ERR_BUSY            = 0xE5;

// Flags (bits 0-6 frozen for Pendulum compat; bit 7+ new in V2)
constexpr uint32_t FLAG_STREAMING   = (1u << 0);
constexpr uint32_t FLAG_RECOVERED   = (1u << 1);
constexpr uint32_t FLAG_BTN_TOGGLED = (1u << 2);
constexpr uint32_t FLAG_DRDY_MISSED = (1u << 3);
constexpr uint32_t FLAG_STATUS_INVALID = (1u << 4);
constexpr uint32_t FLAG_ADS_LOFF_ANY   = (1u << 5);
constexpr uint32_t FLAG_TX_OVERFLOW    = (1u << 6);
constexpr uint32_t FLAG_CONFIG_CHANGED = (1u << 7);

// ADS status word helpers (ADS1299 RDATAC status bytes)
constexpr uint32_t ADS_STATUS_HEADER_MASK = 0xF00000UL;
constexpr uint32_t ADS_STATUS_HEADER_OK   = 0xC00000UL;

enum OutputMode : uint8_t {
  MODE_BIN = 0,
  MODE_CSV = 1
};

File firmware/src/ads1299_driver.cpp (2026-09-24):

#include "ads1299_driver.h"

#include <climits>
#include <cstdio>
#include <SPI.h>

#include "fw_commands.h"
#include "fw_config.h"
#include "fw_protocol.h"
#include "fw_state.h"
#include "fw_tx.h"
#include "fw_utils.h"
#include "fw_watchdog.h"

namespace {

// CONFIG1 encodings used here (HR mode, internal 2.048 MHz clock).
// 0x96 = 250 SPS, 0x95 = 500 SPS, 0x94 = 1000 SPS. Confirmed against the
// ADS1299 datasheet DR table; re-check with a scope if the clock source
// ever changes.
constexpr uint8_t ADS_CONFIG1_250 = 0x96;
constexpr uint8_t ADS_CONFIG1_500 = 0x95;
constexpr uint8_t ADS_CONFIG1_1000 = 0x94;

constexpr uint8_t ADS_CONFIG2_NORMAL = 0xD0;
constexpr uint8_t ADS_CONFIG2_TEST = 0xD3;
// PD_REFBUF=1 (enable internal reference buffer), reserved bits [6:5]=11,
// BIASREF_INT=1, PD_BIAS=1 (enable bias amplifier).
constexpr uint8_t ADS_CONFIG3_INTERNAL_REF_BIAS = 0xEC;
constexpr uint8_t ADS_LOFF_DIAG_CFG = 0x13;
constexpr uint8_t ADS_LOFF_ALL_4CH_MASK = 0x0F;

static inline void adsSelect() { digitalWrite(PIN_SPI_CS, LOW); }
static inline void adsDeselect() { digitalWrite(PIN_SPI_CS, HIGH); }

uint8_t gainToBits(uint8_t gain) {
  switch (gain) {
    case 1: return 0x00;
    case 2: return 0x10;
    case 4: return 0x20;
    case 6: return 0x30;
    case 8: return 0x40;
    case 12: return 0x50;
    case 24:
    default: return 0x60;
  }
}

uint8_t adsChannelConfigValue() {
  uint8_t base = gainToBits(g_adsGain);
  if (g_internalTestSignalEnabled) {
    return static_cast<uint8_t>(base | 0x05);
  }
  return base;
}

uint8_t adsConfig1Value() {
  if (g_sampleRateSps >= 1000) {
    return ADS_CONFIG1_1000;
  }
  if (g_sampleRateSps >= 500) {
    return ADS_CONFIG1_500;
  }
  return ADS_CONFIG1_250;
}

uint8_t adsConfig2Value() {
  return g_internalTestSignalEnabled ? ADS_CONFIG2_TEST : ADS_CONFIG2_NORMAL;
}

uint8_t adsConfig3Value() {
  return ADS_CONFIG3_INTERNAL_REF_BIAS;
}

uint32_t statusLeadOffP(uint32_t status24) {
  return (status24 >> 8) & 0xFF;
}

uint32_t statusLeadOffN(uint32_t status24) {
  return status24 & 0xFF;
}

bool statusHeaderValid(uint32_t status24) {
  return (status24 & ADS_STATUS_HEADER_MASK) == ADS_STATUS_HEADER_OK;
}

bool waitForDrdyEdgeLow(uint32_t timeoutUs) {
  uint32_t start = micros();
  while (digitalRead(PIN_EEG_DRDY) != LOW) {
    fwWatchdogFeed();
    txService();
    if (static_cast<uint32_t>(micros() - start) > timeoutUs) {
      return false;
    }
  }
  return true;
}

void waitDrdyReturnHigh(uint32_t timeoutUs) {
  uint32_t start = micros();
  while (digitalRead(PIN_EEG_DRDY) == LOW) {
    if (static_cast<uint32_t>(micros() - start) > timeoutUs) {
      break;
    }
  }
}

void parseChannelsFromFrame(const uint8_t* frame, int32_t* ch1, int32_t* ch2, int32_t* ch3, int32_t* ch4) {
  *ch1 = signExtend24((static_cast<uint32_t>(frame[3]) << 16) |
                      (static_cast<uint32_t>(frame[4]) << 8) |
                      frame[5]);
  *ch2 = signExtend24((static_cast<uint32_t>(frame[6]) << 16) |
                      (static_cast<uint32_t>(frame[7]) << 8) |
                      frame[8]);
  *ch3 = signExtend24((static_cast<uint32_t>(frame[9]) << 16) |
                      (static_cast<uint32_t>(frame[10]) << 8) |
                      frame[11]);
  *ch4 = signExtend24((static_cast<uint32_t>(frame[12]) << 16) |
                      (static_cast<uint32_t>(frame[13]) << 8) |
                      frame[14]);
}

void resetStreamEdgeStats() {
  noInterrupts();
  g_drdyFlag = false;
  g_lastDrdyTimestampUs = 0;
  g_drdyEdgesTotal = 0;
  interrupts();
  g_missedDrdyFrame = 0;
  g_missedDrdyTotal = 0;
  g_prevDrdyTimestampUs = 0;
  g_drdyIntervalLastUs = 0;
  g_drdyIntervalMinUs = 0xFFFFFFFFUL;
  g_drdyIntervalMaxUs = 0;
  g_drdyJitterAbsLastUs = 0;
  g_drdyJitterAbsMinUs = 0xFFFFFFFFUL;
  g_drdyJitterAbsMaxUs = 0;
  g_drdyIntervalCount = 0;
  g_drdyIntervalSumUs = 0;
  g_drdyJitterAbsSumUs = 0;
}

bool writeChannelMuxAll(uint8_t channelRegValue) {
  adsWriteRegister(REG_CH1SET, channelRegValue);
  adsWriteRegister(REG_CH2SET, channelRegValue);
  adsWriteRegister(REG_CH3SET, channelRegValue);
  adsWriteRegister(REG_CH4SET, channelRegValue);

  return (adsReadRegister(REG_CH1SET) == channelRegValue) &&
         (adsReadRegister(REG_CH2SET) == channelRegValue) &&
         (adsReadRegister(REG_CH3SET) == channelRegValue) &&
         (adsReadRegister(REG_CH4SET) == channelRegValue);
}

void refreshExpectedPeriod() {
  g_expectedPeriodUs = (g_sampleRateSps > 0) ? (1000000UL / g_sampleRateSps) : ADS_DRDY_PERIOD_US;
}

}  // namespace

int32_t adsCountsToMicrovolts(int32_t counts) {
  constexpr int64_t kFullScaleCode = 8388607LL;
  if (g_adsGain == 0) {
    return 0;
  }
  int64_t numerator = static_cast<int64_t>(counts) * static_cast<int64_t>(g_adsVrefUv);
  int64_t denominator = static_cast<int64_t>(g_adsGain) * kFullScaleCode;
  return static_cast<int32_t>(numerator / denominator);
}

void adsSendCommand(uint8_t cmd) {
  SPI.beginTransaction(g_spiSettings);
  adsSelect();
  SPI.transfer(cmd);
  adsDeselect();
  SPI.endTransaction();
  delayMicroseconds(4);
}

uint8_t adsReadRegister(uint8_t reg) {
  SPI.beginTransaction(g_spiSettings);
  adsSelect();
  SPI.transfer(0x20 | (reg & 0x1F));
  SPI.transfer(0x00);
  delayMicroseconds(2);
  uint8_t v = SPI.transfer(0x00);
  adsDeselect();
  SPI.endTransaction();
  delayMicroseconds(2);
  return v;
}

void adsWriteRegister(uint8_t reg, uint8_t value) {
  SPI.beginTransaction(g_spiSettings);
  adsSelect();
  SPI.transfer(0x40 | (reg & 0x1F));
  SPI.transfer(0x00);
  SPI.transfer(value);
  adsDeselect();
  SPI.endTransaction();
  delayMicroseconds(2);
}

void adsReadRegisters(uint8_t startReg, uint8_t count, uint8_t* dest) {
  if (!dest || count == 0) {
    return;
  }
  SPI.beginTransaction(g_spiSettings);
  adsSelect();
  SPI.transfer(0x20 | (startReg & 0x1F));
  SPI.transfer(count - 1);
  delayMicroseconds(2);
  for (uint8_t i = 0; i < count; i++) {
    dest[i] = SPI.transfer(0x00);
  }
  adsDeselect();
  SPI.endTransaction();
  delayMicroseconds(2);
}

bool adsEnsureIdleForRegAccess(bool* wasStreaming) {
  bool was = g_streaming;
  if (wasStreaming) {
    *wasStreaming = was;
  }
  if (was) {
    adsStopStreaming();
    delayMicroseconds(50);
  } else if (g_adsReady) {
    // Even idle, make sure we are out of RDATAC before touching registers.
    adsSendCommand(CMD_SDATAC);
    delayMicroseconds(10);
  }
  return was;
}

void adsHardwareReset() {
  digitalWrite(PIN_EEG_START, LOW);
  digitalWrite(PIN_EEG_RESET, HIGH);
  delay(5);
  digitalWrite(PIN_EEG_RESET, LOW);
  delay(10);
  digitalWrite(PIN_EEG_RESET, HIGH);
  delay(25);
}
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

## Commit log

2026-02-26 Refactor code structure for improved readability and maintainability
    [EEGFrontier.kicad_pcb, EEGFrontier.kicad_sch, Prices.csv]
2026-02-26 Updated PCB images after changed the Header
2026-02-26 Add Gerber job file for EEGFrontier project with specifications and layer details
    [EEGFrontier-B_Cu.gbr, EEGFrontier-B_Mask.gbr, EEGFrontier-B_Paste.gbr, EEGFrontier-B_Silkscreen.gbr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]
2026-02-28 Add EEG processing and visualization components
    - Implemented mne_tools.py for converting sample records to MNE Raw format.
    - Created models.py to define data structures for sample, event, and error packets.
    - Developed pyqt_focus.py for a PyQt-based focus monitoring GUI with real-time EEG data visualization.
    - Added
    eflex_bridge.py to manage the EEG engine instance.
    - Introduced simulator.py to simulate EEG data packets for testing purposes.
    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
2026-03-01 Add band-filtered EEG signal views and redesign dashboard UI
    - add reusable band-pass helpers with scipy/FFT fallback and expose ordered signal views\n- include per-band signal plot points in engine snapshots for raw/gamma/beta/alpha/theta/delta\n- refactor Re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
2026-03-01 Added electrode pin example(check web)
2026-03-01 Clarify external software requirement for filtering and analysis in README.md
2026-04-30 Critical: Fixed float 3V3 #5
    [EEGFrontier-B_Cu.gbr, EEGFrontier-B_Mask.gbr, EEGFrontier-B_Paste.gbr, EEGFrontier-B_Silkscreen.gbr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]
